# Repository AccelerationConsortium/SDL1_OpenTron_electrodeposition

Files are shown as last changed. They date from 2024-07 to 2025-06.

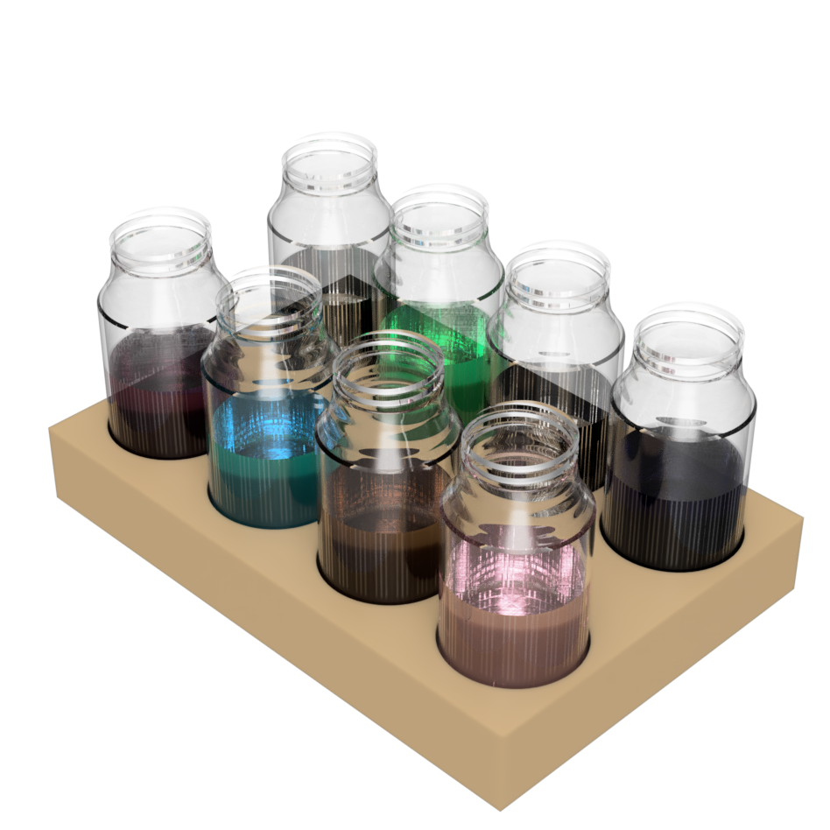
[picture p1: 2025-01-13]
3D_files/vial cartridge/assembly_vial_rack_2024-Sep-16_08-45-49AM-000_CustomizedView3837716591.png

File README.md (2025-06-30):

# SDL1_OpenTron_electrodeposition
This is the repository for the work done by external PhD researcher, Nis Fisker-Bødker from the Danish Technical University (DTU), while working at University of Toronto for the Acceleration Consortium.
The software combines the use of an opentron OT2 and a Sparkfun Arduino Uno to produce a facility for AI optimised electrodeposition of Oxygen Evolution Reaction (OER) catalyst for watersplitting in alkaline environment.

Please pay attention: Due to the Admiral Squidstat software, this will only work on a Windows X86_64 platform and not on Mac/Linux.

# 3D print and machine components
All files used for 3D printing, cutting and ordering at www.hubs.com can be found in /3D_files/. Consider to read the journal article "Democratizing self-driving lab platform for electrodeposition of catalyst and electrochemical validation" to understand the content.

# 1: Installation of Python environment
Install miniconda on your computer. Create an invironment for your opentron:
````
conda create -n opentron python=3.11
conda activate opentron
````

# 2: Download and install the SDL1_OpenTron_electrodeposition experiment
This is what is contained in this particular git-repo.

In a terminal with the correct python environment run:
````
git clone https://github.com/AccelerationConsortium/SDL1_OpenTron_electrodeposition.git
cd SDL1_OpenTron_electrodeposition
pip install -e .
````

# 3: Install requirement: Admiral Squidstat Plus potentiostat
On a Windows X86_64/AMD64 machine install the Admiral Instrument Squidstat software from the .exe file provided by the vendor. Afterwards install the Squidstat wheel provided with this release (/src/SquidstatPyLibrary-1.8.0.5-py3-none-win_amd64.whl) or download the newest wheel file from here:
https://github.com/Admiral-Instruments/AdmiralSquidstatAPI/tree/main/SquidstatLibrary/windows/pythonWrapper/Release

In a terminal within the right python environment and folder, run the command (adjust to your version if you downloaded another version of the wheel file):
````
pip install src/SquidstatPyLibrary-1.8.0.5-py3-none-win_amd64.whl
````

# 4: Install Arduino IDE and test the connection to your Arduino
Refer to Arduino documentation for this step and sparkfun.com for the additional components.
Set the right address for the temperature sensors and the quad relays as found in the firmware in src/arduino/main.ino. Here a summary as pseudocode is shown (don't try to use this directly in a .ino script):
````
// Quad relays
Relay_0-3 = 0x6D  // Default address
Relay_4-7 = 0x6C  // Modified address by programming

// Solid state relays for 110VAC/230VAC
Solid_state = 0x0A  // Default address

// Single relay 8
Relay_8 = 0x18  // Default address

// MCP9600 temperature sensor
tempSensor0 = 0x60  // Default address
tempSensor1 = 0x67  // Modified address by soldering on the PCB
````

Cable everything as according to the schematics in the journal article "AMPERE-2: An open-hardware, robotic platform for automated electrodeposition and electrochemical validation" and in the folder /manuals/Electric_diagram.pdf.
A bill of materials can be found in /manuals/Canada Electrodeposition Bill of Materials (BOM).xlsx

Once the firmware from /src/arduino/ has been uploaded to the Arduino, add a 10 micro farad capacitor between RESET and GND to avoid the PID regulation to reset itself all the time on the board.

# 5: Run the experiment
Examples are provided in /examples to both test the Admiral potentiostat, the Arduino, the opentron and the workflow with all machinary.

Run the experiment from the root of SDL1_OpenTron_electrodeposition/ by executing in an terminal:
````
python example/main.py
````

Please pay attention to the experiment.py. In case you are building your own experiment and workflow, this is the file you must edit to change the workflow of the robot, measurements etc.

# 6: Plotting of data via plot.py
Data (.csv and .jpeg plots) is placed in /data.
If you for some reason need to replot everything run the data/plot.py file.
````
python data/plot.py
````

# Important files
## parameters.py
It is very important to adjust /src/optenTron_electrodeposition/parameters.py to your setup. In here the positions on the openTron deck is defined as well as the chemicals, which relay on the arduino the chemical is attached etc. Spend a decent amount of time to familiarize yourself with the content.
In the future this should be integrated to a general robot_config.json
If you do change anything in parameters.py you must at the root of the SDL1_OpenTron_electrodeposition folder run the command again: 
````
pip install -e .
````

## experiment.py
This is basically the experiment. In the end of the class there is a method named run_experiment() which is basically the recipe of the experiment. Change it according to your needs.

## chemicals_left.txt
First of all sorry: This is a quick workaround to keep track of how much is in the bottles and vials on the setup. The experiment.py checks that it won't run dry by simple volume subtraction.
When refilling chemicals on the setup you must ensure that you also update this file acordingly with the new volumes.
In the future this should be integrated to a general robot_config.json

## last_processed_well.txt
Again sorry: This is a quick workaround to store the last processed well. Usually the openTron notation is eg. A1, A2, etc. but in this case it is from 0-14 with the 15 hole well I've used. Hole 14 is by the way occupied by a temperature sensor, so in reality you can only run from 0-13 wells.
The main reason it was used as a 0-14 number is because it was easier to iterate over numbers. In the future this should be integrated to a general robot_config.json

## metadata.csv
This file basically contains a table of all the experiments, their chemical combination, temperature, timestamp, overpotential during OER reaction at 10 mA/cm2 etc.
I would argue it is a good idea to keep something easy readable and comparable data like this in a single file.

## uid_run_number.txt
Every run has a unique ID which is tracked through this file.
In the future this should be integrated to a general robot_config.json

# Suggestions to future work
* Data should be placed elsewhere.
* SquidstatPyLibrary-XXX.whl should be replaced with an Admiral github and integrated into the pip installation of this repo.
* Move uid_run_number.txt, last_processed_well.txt, chemicals_left.txt, parameters.py into a robot_config.json file.
* Modify main.py to accept .json files with all the experiment variables. This file should then continuesly be populated with metadata about eg. how much was dispensed, in which order, time for each step, measurements etc. as the experiment progress.

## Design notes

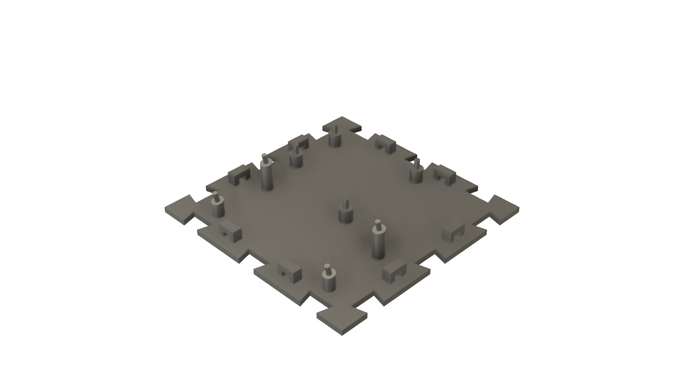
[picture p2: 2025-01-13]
3D_files/electronic tiles/1 arduino_and_screen_tile v14.png

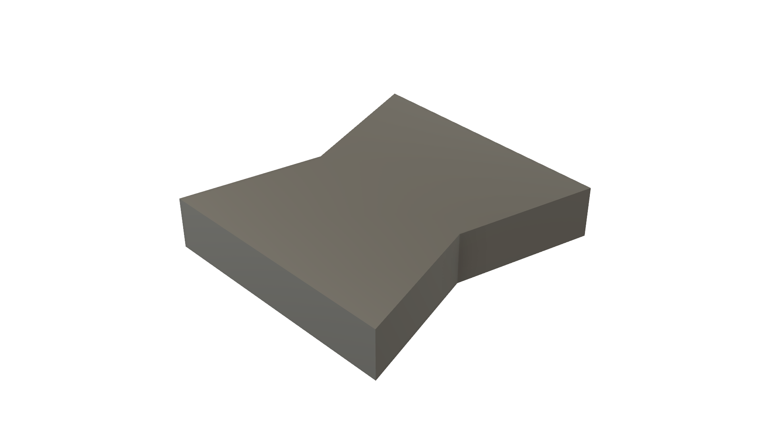
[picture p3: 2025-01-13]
3D_files/electronic tiles/tile_lock v3.png

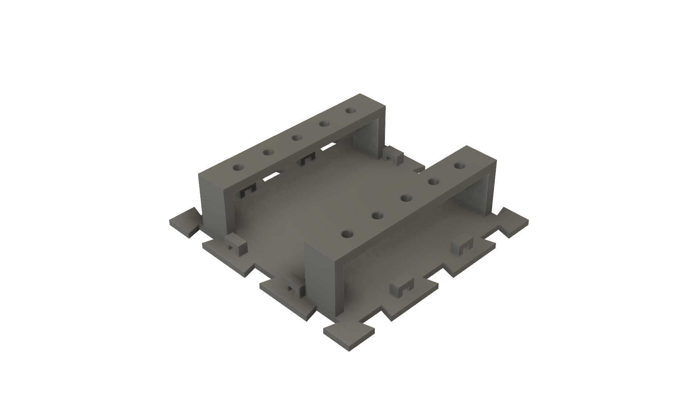
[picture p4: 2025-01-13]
3D_files/electronic tiles/9 terminal_tile v3.png

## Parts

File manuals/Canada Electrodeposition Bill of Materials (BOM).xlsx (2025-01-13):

Bill of Materials, Electrodeposition
Nis Fisker-Bødker, 16-04-2024
Tools |  |  |  |  |  | Minimum viable product | Fully utilized openTron
 | Item | Link | Cost per quantity | Quantity | Total
 | Makita Driver Drill | https://www.amazon.ca/Makita-DHP482Z-Hammer-Driver-Drill/dp/B01C85KSVU | 99.99 CAD | 1 | 99.99 CAD
 | Makita Battery | https://www.amazon.ca/Makita-Y-00309-Li-Ion-Battery-Charger/dp/B075SM1LHH | 127.00 CAD | 1 | 127.00 CAD
 | Tap drill set | https://www.amazon.ca/Neiko-10059A-Combination-Change-Adapter/dp/B0762HJ3GF | 45.00 CAD | 1 | 45.00 CAD
 | Drill set | https://www.amazon.ca/Bosch-CO21-Cobalt-Metal-Drill/dp/B06XY7W87H | 55.00 CAD | 1 | 55.00 CAD
 | Conedrill etc | https://www.amazon.ca/NordWolf-12-Piece-Countersink-Automatic-Compatible/dp/B083NWL5D2 | 60.00 CAD | 1 | 60.00 CAD
 | Metal saw | https://www.amazon.ca/Craftsman-Hand-12-Inch-Hacksaw-CMHT20138/dp/B07R92S9YZ | 16.00 CAD | 1 | 16.00 CAD
 | Estimated freight |  |  |  | 40.30 CAD
 | Total |  |  |  | 443.29 CAD
Hardware | Cartridge base
 | Item | Link | Cost per quantity | Quantity | Total
 | Aluminum base (bottom) | hubs.com | 110.00 CAD | 2 | 220.00 CAD
 | Aluminum base (top) | hubs.com | 110.00 CAD | 2 | 220.00 CAD
 | M3 8x8 Rubber shock absorbers | https://www.amazon.ca/Rubber-Absorber-Vibration-Silentblock-Bobbins/dp/B07H2BW3CX | 9.17 CAD | 2 | 18.34 CAD
 | Ultrasonic transducer | https://www.amazon.ca/Baglaum-Ultrasonic-Transducer-Cleaning-Machines/dp/B0CRYQLTQN | 50.23 CAD | 2 | 100.46 CAD
 | Flat heating element 110V | https://www.amazon.ca/PTCYIDU-Insulated-Temperature-Thermostatic-Miniature/dp/B0CDKTLXWJ | 26.92 CAD | 2 | 53.84 CAD
 | Pt100 thermocouple | https://www.sparkfun.com/products/251 | 17.00 CAD | 2 | 34.00 CAD
 | Temperature sensor MCP9600 | https://www.sparkfun.com/products/16295 | 22.50 CAD | 2 | 45.00 CAD
 | Nickel Pt100 sleeve (corossion resistant) | https://www.amazon.com/Temperature-Deep-Drawing-DS18B20-Thermowell-ThermocoupleProtection/dp/B0C61VT83G | 20.00 CAD | 1 | 20.00 CAD
 | Aluminum rod ø10mm | https://www.amazon.ca/MECCANIXITY-Round-Aluminum-Diameter-Length/dp/B09Y24WWGP | 20.00 CAD | 2 | 40.00 CAD
 | M3, M4 screws flat head | https://www.amazon.ca/Hilitchi-460-Piece-Metric-Countersunk-Assortment/dp/B06Y3JDM4R | 23.00 CAD | 1 | 23.00 CAD
 | M4 threaded rod 60mm | https://www.amazon.ca/uxcell-Threaded-Stainless-Threads-M4-0-7/dp/B09L68MJJ5 | 9.00 CAD | 1 | 9.00 CAD
 | Sparkfun Arduino | https://www.sparkfun.com/products/18158 | 21.50 CAD | 1 | 21.50 CAD
 | Sparkfun LCD | https://www.sparkfun.com/products/16396 | 22.00 CAD | 1 | 22.00 CAD
 | Sparkfun AC Solid state relay 110V | https://www.sparkfun.com/products/16810 | 95.00 CAD | 1 | 95.00 CAD
 | Sparkfun Qwiic cable | https://www.sparkfun.com/products/15081 | 9.00 CAD | 1 | 9.00 CAD
 | M3, M4 washers | https://www.amazon.ca/260-Pcs-7-Size-QTEATAK-Stainless-Assortment/dp/B07LCB92CB | 14.00 CAD | 1 | 14.00 CAD
 | M4 wing nut | https://www.amazon.ca/uxcell-Stainless-Fasteners-Hurrican-Butterfly/dp/B07QB5NKDG | 13.50 CAD | 1 | 13.50 CAD
 | Heat paste | https://www.amazon.ca/BSFF-Compound-Heatsink-Processor-Performance/dp/B09NLXX61M | 16.00 CAD | 1 | 16.00 CAD
 | Estimated freight |  |  |  | 95.86 CAD
 | Total |  |  |  | 1070.50 CAD | 1070.50 CAD | 11775.54 CAD
Hardware | Well cartridge
 | Item | Link | Cost per quantity | Quantity | Total
 | Aluminum base | xometry.com | 110.00 CAD | 1 | 110.00 CAD
 | Nickel tape 0,2mm thickness | https://www.amazon.ca/GOONSDS-Nickel-Plate-Sheet-0-2x100x1000mm/dp/B09879LSZC | 69.00 CAD | 1 | 69.00 CAD
 | Double sided tape | https://www.amazon.ca/Premium-Double-Sided-Adhesive-Tape/dp/B07B5YBN3Y | 15.50 CAD | 1 | 15.50 CAD
 | Gasgets | https://www.amazon.ca/uxcell-Silicone-Ring-Width-Gasket/dp/B07CVJMN2M | 8.99 CAD | 2 | 17.98 CAD
 | PP plastic top | xometry.com | 376.00 CAD | 1 | 376.00 CAD
 | (alternatively PEEK) | hubs.com | 576.00 CAD | 0 | 0.00 CAD
 | Estimated freight |  |  |  | 58.85 CAD
 | Total |  |  |  | 647.33 CAD | 647.33 CAD | 6473.28 CAD
Hardware | Robotic mount
 | Item | Link | Cost per quantity | Quantity | Total
 | Nickel rod ø 10mm | https://www.amazon.ca/RINGGLO-Antioxidant-Activity-Scientific-Experiment/dp/B0CCMD16QV | 35.87 CAD | 1 | 35.87 CAD
 | Mini Hydroflex reference electrode | https://gaskatel.de/en/shop/mini-hydrogen-reference-electrode-mini-hydroflex/ | 308.00 CAD | 1 | 308.00 CAD
 | Platinum electrode | https://www.amazon.ca/Platinum-Electrode-99-99-10mm-Customized-Specifications/dp/B0CP8XHCZ6 | 285.00 CAD | 1 | 285.00 CAD
 | Platinum wire | https://www.amazon.ca/Platinum-Wire-gauge-99-9-6-inches/dp/B003E2Y2T6 | 56.00 CAD | 1 | 56.00 CAD
 | Electrical wire | https://www.amazon.ca/CBAZY-Stranded-Flexible-Silicone-Electric/dp/B073RDG2J6 | 25.00 CAD | 1 | 25.00 CAD
 | Solder connecters | https://www.amazon.ca/Connectors-Sopoby-Waterproof-Electrical-Automotive/dp/B07R4Z13P3 | 30.00 CAD | 1 | 30.00 CAD
 | Wire connectors | https://www.amazon.ca/Compact-Splicing-Connector-Assortment-221-2401/dp/B0BXQG6RLQ | 58.42 CAD | 1 | 58.42 CAD
 | Banana plug terminals | https://www.amazon.ca/Speaker-Terminal-Binding-Adapter-Connector/dp/B07C2P4YNB | 12.09 CAD | 1 | 12.09 CAD
 | Hoop and loop tape | https://www.amazon.ca/gp/product/B0BZXMHKRB/ref=ewc_pr_img_1?smid=AHCEK5ZEJTURN&psc=1 | 24.99 CAD | 1 | 24.99 CAD
 | Single relay to switch between Counter and Reference | https://www.sparkfun.com/products/15093 | 20.00 CAD | 1 | 20.00 CAD
 | Qwiic multiplexer | https://www.sparkfun.com/products/18012 | 3.00 CAD | 3 | 9.00 CAD
 | Qwiic long cables | https://www.sparkfun.com/products/17257 | 3.00 CAD | 3 | 9.00 CAD
 | Cable shoes | https://www.amazon.ca/Disconnect-Electrical-Solderless-Connectors-Assortment/dp/B01E4RAVI0 | 22.00 CAD | 1 | 22.00 CAD
 | DC connector for quad relay | https://www.sparkfun.com/products/10287 | 3.50 CAD | 2 | 7.00 CAD
 | Plate for supporting electronics |  | 110.00 CAD | 1 | 110.00 CAD
 | Machine shop cut of 8x Ø10mm alu legs incl. tapping M3 |  | 80.00 CAD | 1 | 80.00 CAD
 | 3D printer filament |  | 40.00 CAD | 2 | 80.00 CAD
 | 3D resin printing of flush tool |  | 40.00 CAD | 1 | 40.00 CAD
 | Estimated freight |  |  |  | 81.04 CAD
 | Total |  |  |  | 1293.41 CAD | 1293.41 CAD | 1293.41 CAD
Hardware | Cleaning cartridge
 | Item | Link | Cost per quantity | Quantity | Total
 | PP plastic top | xometry.com | 300.00 CAD | 1 | 300.00 CAD
 | Aluminum base | xometry.com | 110.00 CAD | 1 | 110.00 CAD
 | Peristaltic pump | https://www.amazon.ca/peristaltic-Kamoer-KPHM100-Service-high-Precision/dp/B09F69KYF3 | 20.00 CAD | 6 | 120.00 CAD
 | Silicone tubing 5mm OD, 3mm ID | https://www.amazon.ca/Yesallwas-Silicone-Flexible-Rubber-Transfer/dp/B07S5LL4HR | 16.00 CAD | 1 | 16.00 CAD
 | 12V DC supply | https://www.amazon.ca/Waterproof-Converter-Transformer-Voltage-3-Prong/dp/B08ZJZPF4Y | 44.00 CAD | 1 | 44.00 CAD
 | 12V relay | https://www.sparkfun.com/products/16566 | 32.50 CAD | 2 | 65.00 CAD
 | Cable zip ties | https://www.amazon.ca/BESTIN-Self-Locking-Black-Nylon-12-Inch/dp/B0977LP2KQ | 19.00 CAD | 1 | 19.00 CAD
 | Estimated freight |  |  |  | 67.40 CAD
 | Total |  |  |  | 741.40 CAD | 741.40 CAD | 741.40 CAD
Chemicals | Consumables
 | Item | Link | Cost per quantity | Quantity | Total
 | 500 FeCl3 |  | 592.00 CAD | 1 | 592.00 CAD
 | 500g CoCl2 salt |  | 43.00 CAD | 1 | 43.00 CAD
 | 500g ZnCl3 |  | 108.00 CAD | 1 | 108.00 CAD
 | 100 g CuCl2 |  | 50.00 CAD | 1 | 50.00 CAD
 | 500g MnCl2 |  | 64.00 CAD | 1 | 64.00 CAD
 | 125g CrCl3 |  |  | 1 | 0.00 CAD
 | 500g NiCl2 |  |  | 1 | 0.00 CAD
 | 4L Ammonium hydroxide NH4OH |  |  | 1 | 0.00 CAD
 | 500g potassium citrate |  |  | 1 | 0.00 CAD
 | Hydrocloric aeid 1M / 1N 2L |  |  | 1 | 0.00 CAD
 | DI water 8L |  |  | 1 | 0.00 CAD
 | Bottles for chemicals 6+9 500ml |  | 64.00 CAD | 2 | 128.00 CAD
 | Chemstore misc. Like beakers, vials etc. |  | 206.00 CAD | 1 | 206.00 CAD
 | Estimated freight |  |  |  | 85.70 CAD
 | Total |  |  |  | 1276.70 CAD | 1276.70 CAD | 1276.70 CAD
 |  |  |  |  |  | 5029.34 CAD | 21560.33 CAD

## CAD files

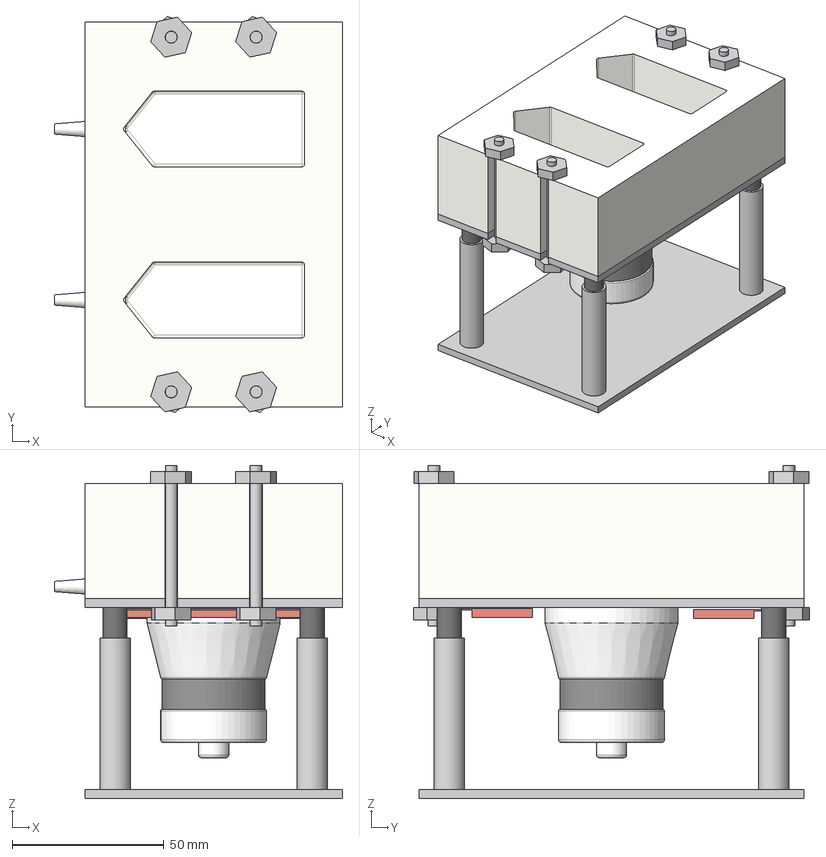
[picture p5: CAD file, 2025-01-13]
3D_files/cleaning cartridge/assembly_cleaning_cartridge v15.step
95.0 x 130.6 x 110.0 mm
cleaning_bath_bolt x 4
cartridge_bottom
rubber_dampener x 4
alu_legs x 4
cartridge_top
ultrasound
heating_element
heating_element_rotated
Cleaning_bath

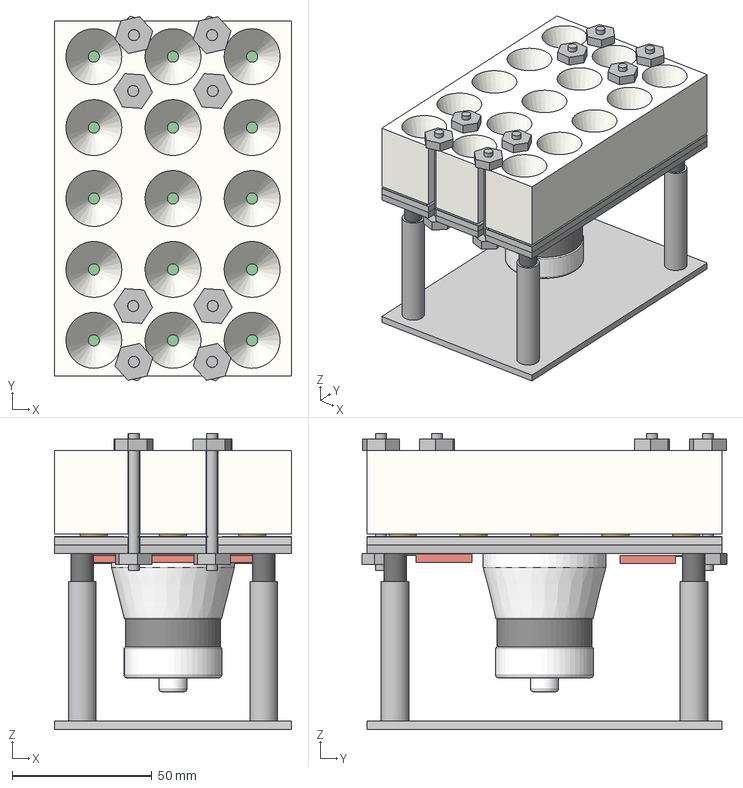
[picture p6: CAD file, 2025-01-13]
3D_files/well cartridge/assembly_well_cartridge v44.step
85.0 x 130.6 x 106.0 mm
well_cartridge_bolt x 4
cartridge_bottom
rubber_dampener x 4
alu_legs x 4
cartridge_top
ultrasound
heating_element
heating_element_rotated
nickel_layer x 3
1_well_catridge_ultrasound_mount
well_cartridge_bolt_top x 4
3_well_cartridge_test_cell

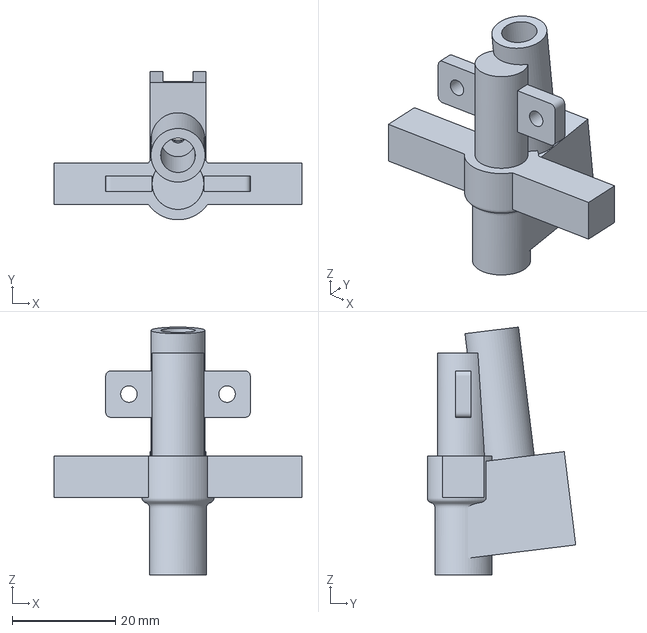
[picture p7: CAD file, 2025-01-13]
3D_files/3Dprint/platinum_silver_electrode v7.3mf
48.0 x 28.7 x 48.0 mm

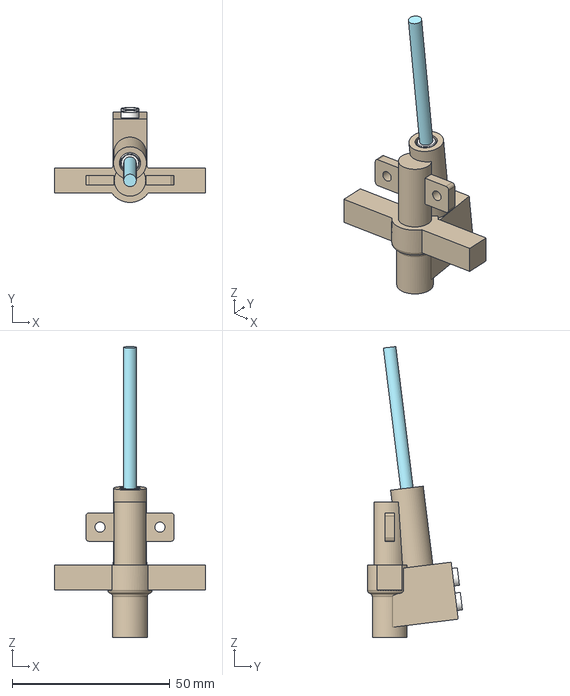
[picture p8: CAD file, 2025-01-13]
3D_files/agcl electrode tool/platinum_silver_electrode v9.step
48.0 x 30.1 x 92.2 mm
cable_terminal
silver_reference_electrode

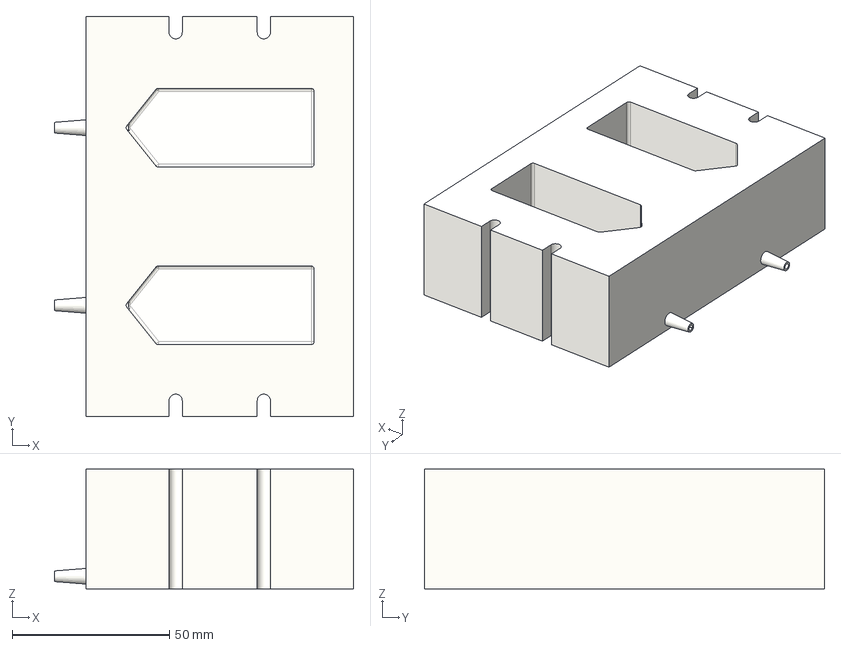
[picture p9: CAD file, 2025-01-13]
3D_files/Cleaning_bath v7.step
95.0 x 127.0 x 38.0 mm

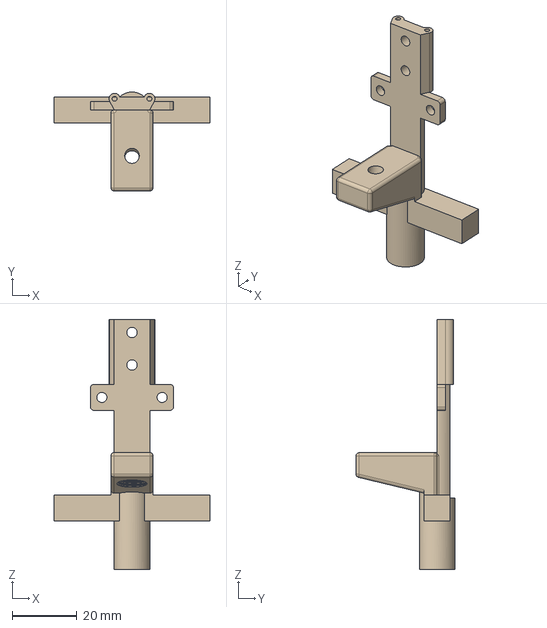
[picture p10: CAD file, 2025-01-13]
3D_files/electrochemical test tool/platinum_electrode v46.step
48.0 x 30.5 x 77.0 mm

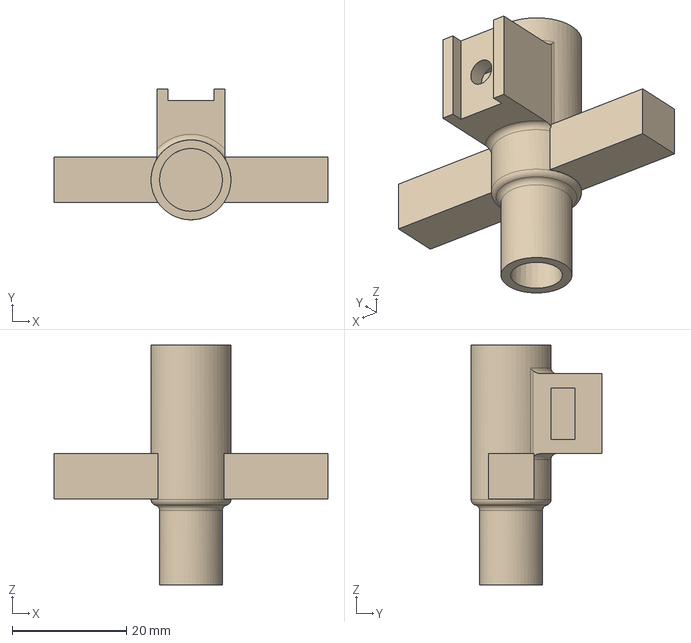
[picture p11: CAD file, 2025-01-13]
3D_files/electrodeposition tool/nickel_electrode v30.step
48.0 x 22.9 x 42.0 mm

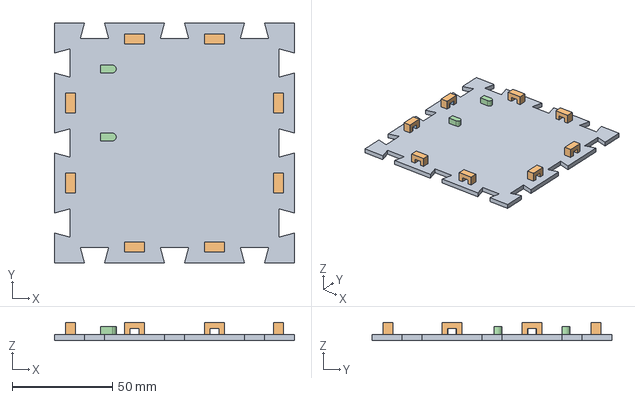
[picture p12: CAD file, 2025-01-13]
3D_files/electronic tiles/4 Power_source1 v18.step
120.0 x 120.0 x 9.00 mm

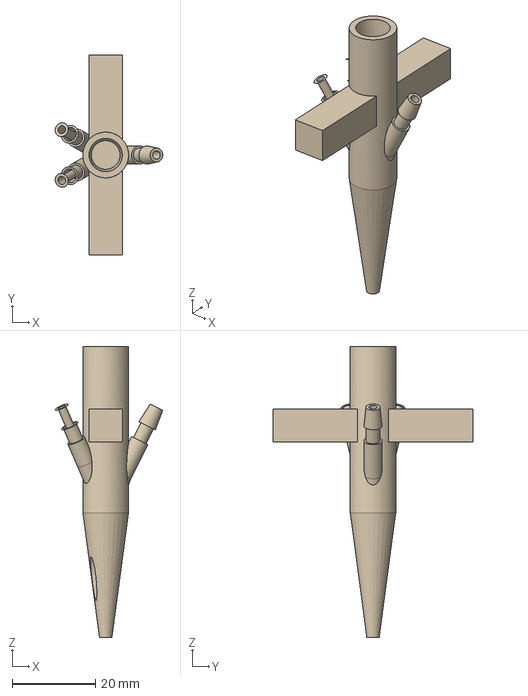
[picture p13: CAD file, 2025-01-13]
3D_files/flush tool/Flush_tool v11.step
25.9 x 48.0 x 70.0 mm

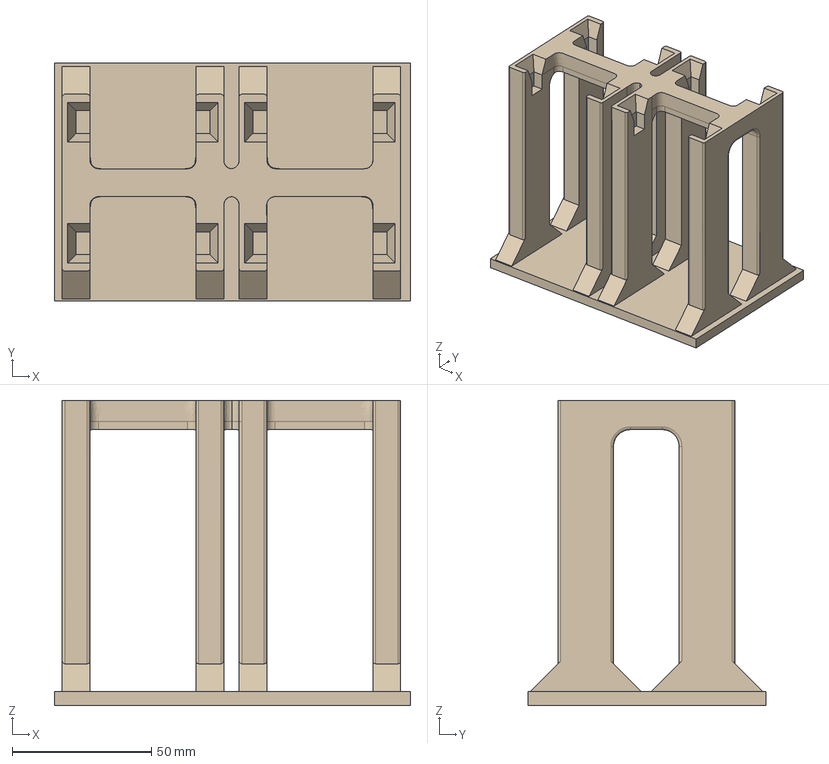
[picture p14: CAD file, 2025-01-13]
3D_files/tool cartridge/tool_cartridge_v7.step
127.8 x 85.5 x 109.5 mm

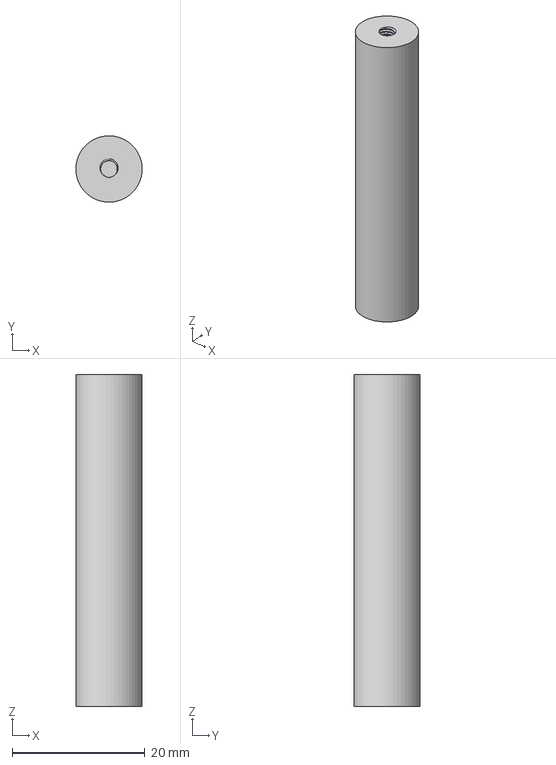
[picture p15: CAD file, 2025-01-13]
3D_files/ultrasonic cartridge base/alu_legs v3.step
9.99 x 10.00 x 50.0 mm

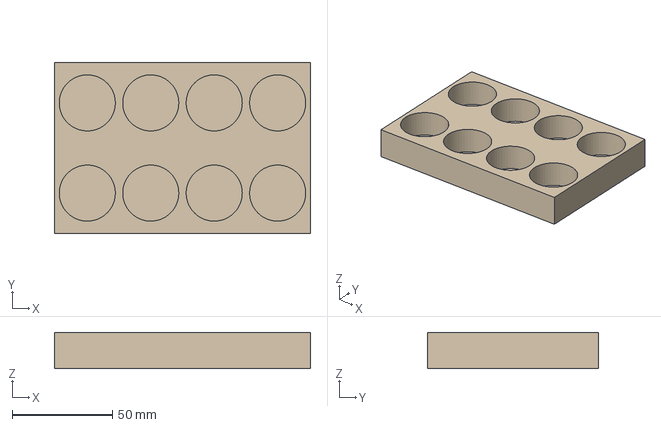
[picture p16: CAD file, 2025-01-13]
3D_files/vial cartridge/vial_rack v3.step
127.8 x 85.5 x 18.0 mm

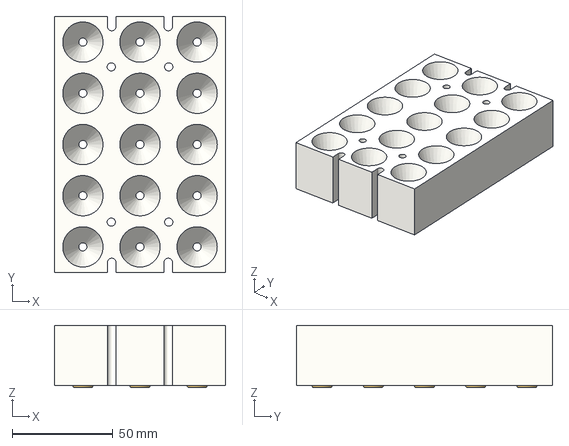
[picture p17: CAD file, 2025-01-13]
3D_files/well cartridge/well_cartridge_v24_CNCmachined_PE.step
85.0 x 127.0 x 31.0 mm

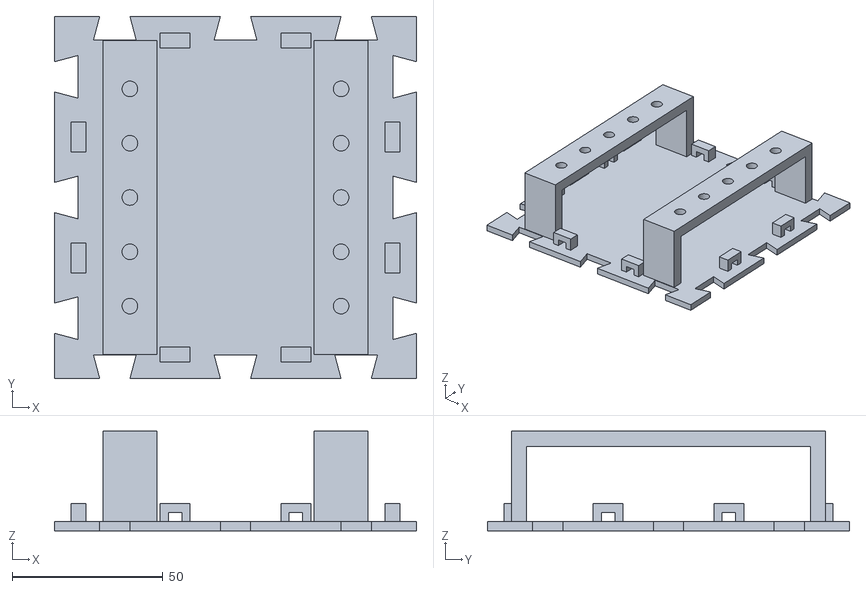
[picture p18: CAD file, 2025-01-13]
3D_files/3Dprint/9 terminal_tile v2.stl
120.0 x 120.0 x 33.0

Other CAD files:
3D_files/agcl electrode tool/platinum_silver_electrode v9 -only_plastic_for_printing.step
3D_files/cartridge_bottom v1.step
3D_files/cleaning cartridge/Cleaning_bath v9.step
3D_files/1_well_catridge_ultrasound_mount v5.step
3D_files/3Dprint/1 arduino_and_screen_tile v12.stl
3D_files/3Dprint/3_well_cartridge_test_cell v21.stl
3D_files/3Dprint/Cleaning_bath v7.stl
3D_files/3Dprint/Electrical_connections v5.stl
3D_files/3Dprint/Flush_tool_Eloise v10.stl
3D_files/3Dprint/Flush_tool_Eloise v7.stl
3D_files/3Dprint/Flush_tool_Eloise v9.stl
3D_files/3Dprint/Power_source1 v16.stl
3D_files/3Dprint/Power_source2 v11.stl
3D_files/3Dprint/Quad_relay v6.stl
3D_files/3Dprint/Thread test v1.stl
3D_files/3Dprint/alu_legs v3.stl
3D_files/3Dprint/arduino_and_screen_tile v9.stl
3D_files/3Dprint/cleaning_cartridge_bracket v2.stl
3D_files/3Dprint/cleaning_cartridge_bracket v3.stl
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

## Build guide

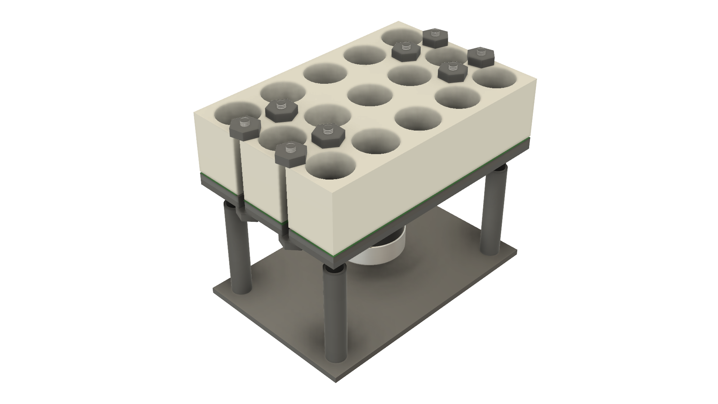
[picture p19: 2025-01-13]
3D_files/well cartridge/assembly_well_cartridge v44.png

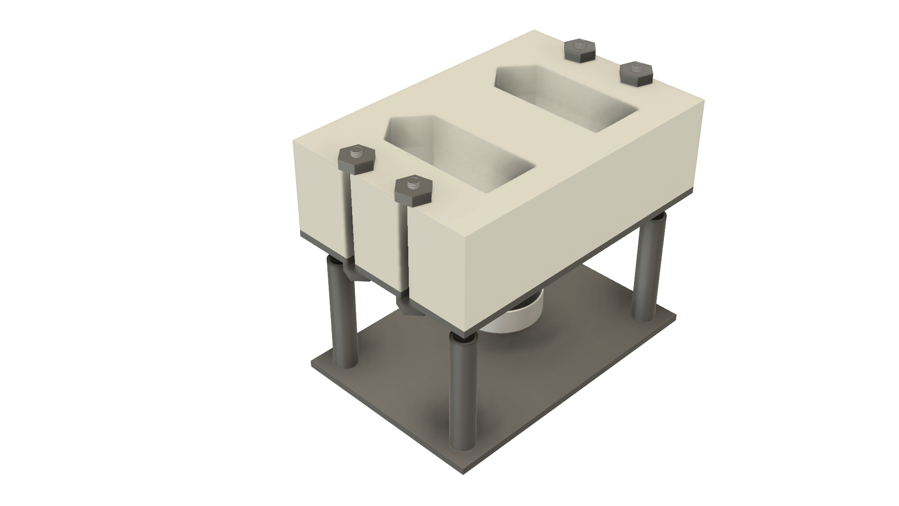
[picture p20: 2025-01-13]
3D_files/cleaning cartridge/assembly_cleaning_cartridge v14.png

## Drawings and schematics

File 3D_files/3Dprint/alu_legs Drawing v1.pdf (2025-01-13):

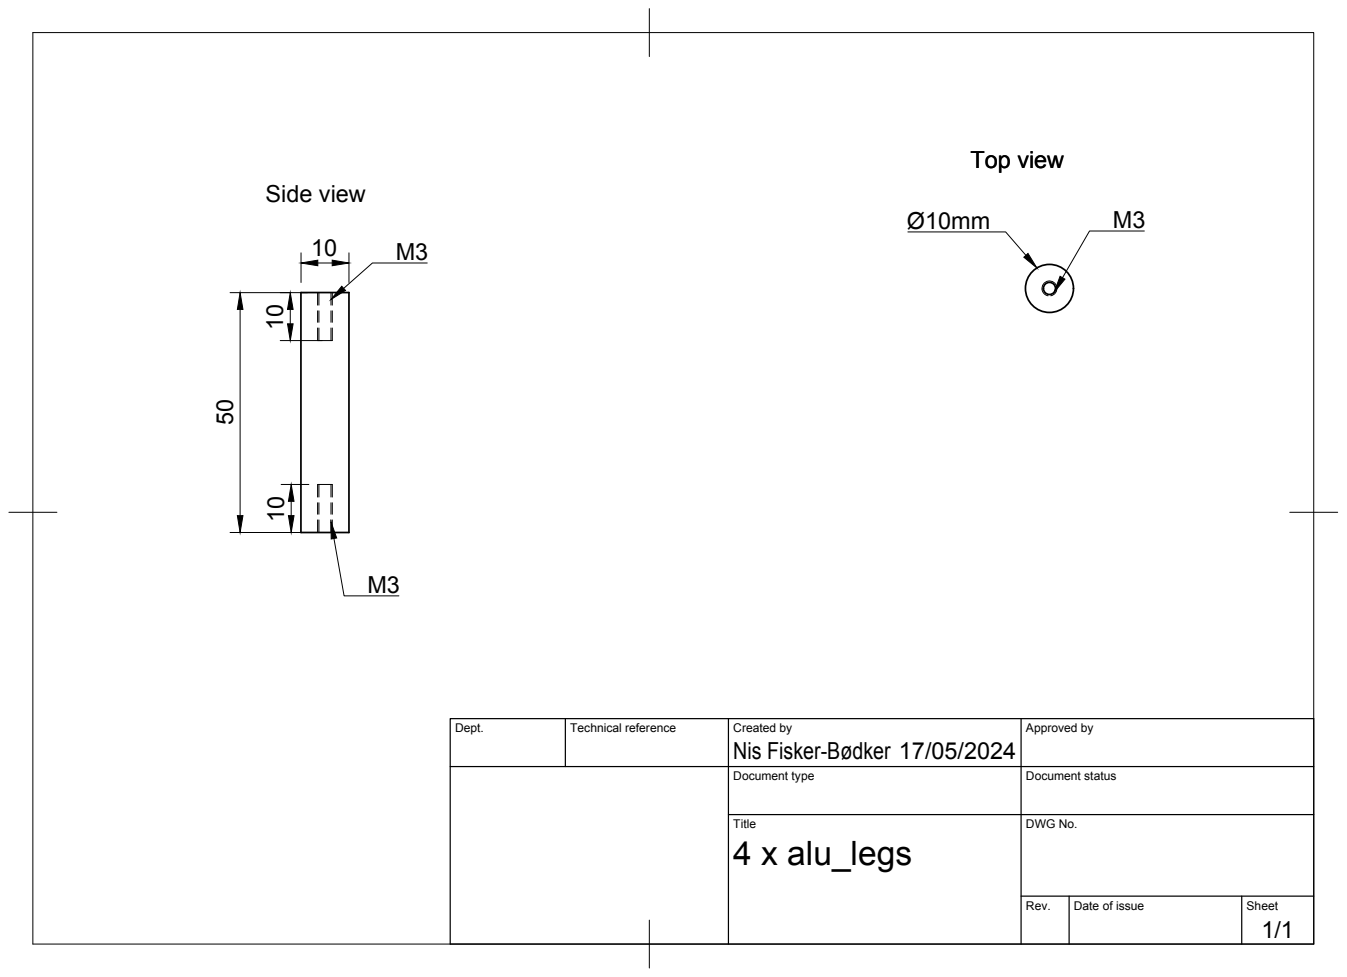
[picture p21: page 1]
Top view; Side view

Dept. | Technical reference | Created by Nis Fisker-Bødker 17/05/2024 | Approved by

Document type | Document status

Title 4 x alu_legs | DWG No.

Rev. | Date of issue | Sheet 1/1

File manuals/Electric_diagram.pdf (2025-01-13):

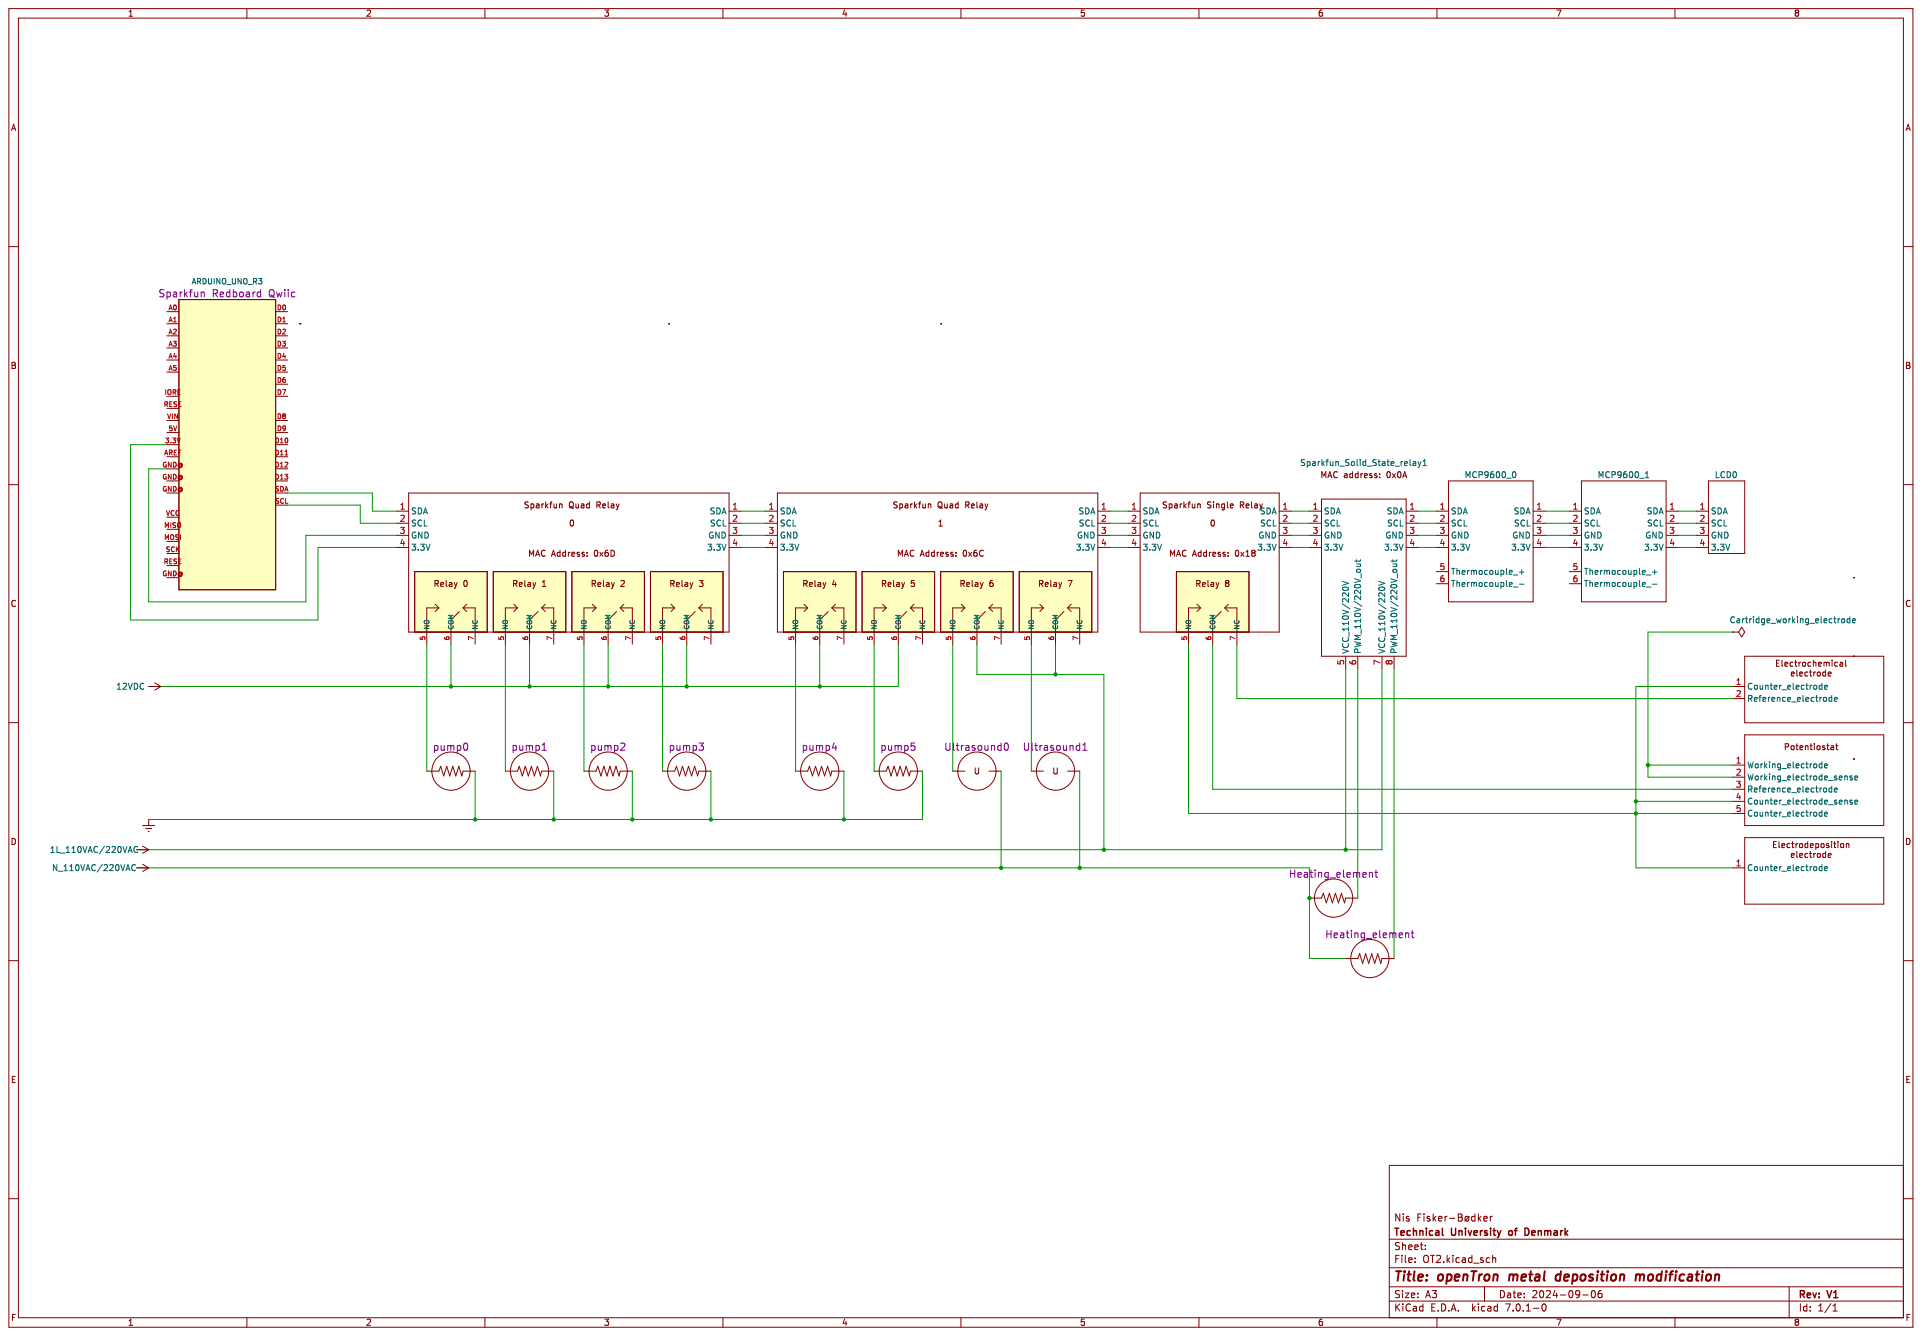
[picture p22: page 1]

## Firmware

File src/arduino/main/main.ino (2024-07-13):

/*
  Software written by
  Nis Fisker-Bødker
  nis.fisker@gmail.com
  2024 at University of Toronto

  Components used:
  Sparkfun Arduino Redboard with Qwiic
  2 x SparFun MCP9600 (for temperature measurements in liquids)
  1 x SparkFun Dual Solid State Relay (for heat control)
  1 x Sparkfun Quad Relay (for control of peristaltic pumps)
  1 x Sparkfun SerLCD
  1 x Sparkfun single relay (for control of electrode connection)

*/
#include <Wire.h>
#include <EEPROM.h>
const byte buff_size = 40;
char input_buffer[buff_size];
const char start_marker = '<';
const char end_marker = '>';
byte bytes_rcvd = 0;
boolean read_in_progress = false;
boolean new_data_pc = false;
String message_from_pc;
int direction_in = 0;
int steps_in = 0;
int step_time_in = 0;
int m_num = 0;
float ultrasound_time_in;


/*
   Load temperature sensor
*/
#include <SparkFun_MCP9600.h>
MCP9600 tempSensor0;
float sample_temperature0;
float ambient_temperature0;
MCP9600 tempSensor1;
float sample_temperature1;
float ambient_temperature1;

/*
   Load LCD
*/

#include <SerLCD.h>
SerLCD lcd;  // Initialize the library with default I2C address 0x72


/*
   Load relays
*/
// Relay 0-3
#include <SparkFun_Qwiic_Relay.h>
#define RELAY_ADDR 0x6D  // Alternate address 0x6C
Qwiic_Relay quadRelay(RELAY_ADDR);

// Solid state relays for 110VAC
#define RELAY_SOLIDSTATE 0x0A
Qwiic_Relay solidStateRelay(RELAY_SOLIDSTATE);

// Relay 4-7
// Remember this is NOT a standard I2C add - it was coded to the quad relay.
#define RELAY_ADDR2 0x6C  // 0x09
Qwiic_Relay quadRelay2(RELAY_ADDR2);

// Relay 8
#define RELAY_ADDR3 0x18
Qwiic_Relay singleRelay3(RELAY_ADDR3);

/*
   Load PID control
*/
#include <AutoPID.h>
#define OUTPUT_MIN 0
#define OUTPUT_MAX 255
#define KP0 .12
#define KI0 0.5
#define KD0 1
#define KP1 .12
#define KI1 0.5
#define KD1 1
double temperature0, outputVal0;
double temperature1, outputVal1;
double setPoint0;
double setPoint1;
AutoPID PID0(&temperature0, &setPoint0, &outputVal0, OUTPUT_MIN, OUTPUT_MAX, KP0, KI0, KD0);
AutoPID PID1(&temperature1, &setPoint1, &outputVal1, OUTPUT_MIN, OUTPUT_MAX, KP1, KI1, KD1);
unsigned long lastTempUpdate;  //tracks clock time of last temp update
int dutyCycle0 = 0;            //Tracks how much the relay is on at 1Hz. 120 = 100%.
int dutyCycle1 = 0;            //Tracks how much the relay is on at 1Hz. 120 = 100%.

void setup() {
  Serial.begin(115200);
  Wire.begin();
  Wire.setClock(100000);


  /*
     Setup LCD
  */
  // Serial.println("Booting LCD");
  lcd.begin(Wire);                  //Set up the LCD for I2C communication
  lcd.setBacklight(255, 255, 255);  //Set backlight to bright white
  lcd.setContrast(5);               //Set contrast. Lower to 0 for higher contrast.
  lcd.clear();                      //Clear the display - this moves the cursor to home position as well
  lcd.print("Booting!");


  /*
     Setup relays
  */
  if (!quadRelay.begin()) {
    lcd.setCursor(0, 0);
    lcd.print("Quad relay not connected");
    Serial.println("Check connections to Qwiic Relay 0-3.");
    delay(2000);
  }
  if (!solidStateRelay.begin()) {
    lcd.setCursor(0, 0);
    lcd.print("SolStateRelay not connected");
    Serial.println("Check connections to solid state relay.");
    delay(2000);
  }
  if (!quadRelay2.begin()) {
    lcd.setCursor(0, 0);
    lcd.print("Quad relay not connected");
    Serial.println("Check connections to Qwiic Relay 4-7.");
    delay(2000);
  }
  if (!singleRelay3.begin()) {
    lcd.setCursor(0, 0);
    lcd.print("Single relay not connected");
    Serial.println("Check connections to Qwiic Relay 8.");
    delay(2000);
  }

  /*
     Setup temperature sensor 0
  */
  // Serial.println("Booting temperature sensors");
  tempSensor0.begin(0x60);  // Uses the default address (0x60) for SparkFun Thermocouple Amplifier
  tempSensor1.begin(0x67);

  // Check if temperature sensor is connected
  // Serial.println("Check if temperature sensor 0 is online");
  if (!tempSensor0.isConnected()) {
    lcd.setCursor(0, 0);
    lcd.print("Temp 0 not connected");
    Serial.println("Temperature sensor 0 not connected");
    delay(10000);
  }

  // Check if the temperature sensor address is correct
  // Serial.println("Check temperature sensor 0 address");
  if (!tempSensor0.checkDeviceID()) {
    lcd.setCursor(0, 0);
    lcd.print("Temp 0 addr. is wrong");
    Serial.println("Temperature sensor 0 address is wrong");
    delay(10000);
  }


  /*
     Setup temperature sensor 1
  */
  // Check if temperature sensor 1 is connected
  // Serial.println("Check if temperature sensor 1 is online");
  if (!tempSensor1.isConnected()) {
    lcd.setCursor(0, 0);
    lcd.print("Temp 1 not connected");
    Serial.println("Temperature sensor 1 not connected");
    delay(10000);
  }

  // Check if the temperature sensor address is correct
  // Serial.println("Check temperature sensor 1 address");
  if (!tempSensor1.checkDeviceID()) {
    lcd.setCursor(0, 0);
    lcd.print("Temp 1 addr. is wrong");
    Serial.println("Temperature sensor 1 address is wrong");
    delay(10000);
  }



  /*
     Setup PID control
  */
  read_from_eeprom_setPoints();

  // if temperature is more than 4 degrees below or above setpoint, OUTPUT will be set to min or max respectively
  PID0.setBangBang(2);
  PID1.setBangBang(2);
  //set PID update interval to 1200ms
  PID0.setTimeStep(1200);
  PID1.setTimeStep(1200);

  lcd.clear();
}

void loop() {
  // Updating the sensor values
  delay(1000);
  sample_temperature0 = read_sample_temperature(0);
  sample_temperature1 = read_sample_temperature(1);



  // Update PID controller 0
  temperature0 = sample_temperature0;
  PID0.run();
  if (outputVal0 > 0) {
    dutyCycle0 = (outputVal0 / 255) * 120;
  } else {
    dutyCycle0 = 0;
  }
  solidStateRelay.setSlowPWM(1, dutyCycle0);

  // Update PID controller 1
  temperature1 = sample_temperature1;
  PID1.run();
  if (outputVal1 > 0) {
    dutyCycle1 = (outputVal1 / 255) * 120;
  } else {
    dutyCycle1 = 0;
  }
  solidStateRelay.setSlowPWM(2, dutyCycle1);

  // Write the sensor values to the LCD
  write_to_lcd(sample_temperature0, sample_temperature1, dutyCycle0, dutyCycle1);


  // Check if there is instructions from the PC
  get_data_from_pc();
}

void get_data_from_pc() {

  // receive data from PC and save it into input_buffer
  while (Serial.available()) {
    char x = Serial.read();

    // the order of these IF clauses is significant

    if (x == end_marker) {
      read_in_progress = false;
      new_data_pc = true;
      input_buffer[bytes_rcvd] = 0;
      parse_data();
    }

    if (read_in_progress) {
      input_buffer[bytes_rcvd] = x;
      bytes_rcvd++;
      if (bytes_rcvd == buff_size) {
        bytes_rcvd = buff_size - 1;
      }
    }

    if (x == start_marker) {
      bytes_rcvd = 0;
      read_in_progress = true;
    }
  }
}

void parse_data() {
  // split the data into its parts
  char *str_to_ind;  // this is used by strtok() as an index

  str_to_ind = strtok(input_buffer, ",");  // get the first part - the string
  message_from_pc = String(str_to_ind);

  if (message_from_pc == "set_relay_on_time") {
    str_to_ind = strtok(NULL, ",");    // this continues where the previous call left off
    int relay_num = atoi(str_to_ind);  // convert this part to an integer

    str_to_ind = strtok(NULL, ",");
    int time_ms = atoi(str_to_ind);

    if (0 <= relay_num && relay_num <= 3)  // First quad relay
    {
      int relay = relay_num + 1;
      quadRelay.turnRelayOn(relay);
      delay(time_ms);
      quadRelay.turnRelayOff(relay);
    }
    if (4 <= relay_num && relay_num <= 7)  // Second quad relay
    {
      int relay = relay_num - 3;
      quadRelay2.turnRelayOn(relay);
      delay(time_ms);
      quadRelay2.turnRelayOff(relay);
    }
    if (8 == relay_num)  // Single relay
    {
      singleRelay3.turnRelayOn();
      delay(time_ms);
      singleRelay3.turnRelayOff();
    }
    Serial.println("#");  // '#' indicates process is done
  }

  if (message_from_pc == "set_relay_on") {
    str_to_ind = strtok(NULL, ",");    // this continues where the previous call left off
    int relay_num = atoi(str_to_ind);  // convert this part to an integer

    if (0 <= relay_num && relay_num <= 3)  // First quad relay
    {
      int relay = relay_num + 1;
      quadRelay.turnRelayOn(relay);
    }
    if (4 <= relay_num && relay_num <= 7)  // Second quad relay
    {
      int relay = relay_num - 3;
      quadRelay2.turnRelayOn(relay);
    }
    if (8 == relay_num)  // Single relay
    {
      singleRelay3.turnRelayOn();
    }
    Serial.println("#");  // '#' indicates process is done
  }

  if (message_from_pc == "set_relay_off") {
    str_to_ind = strtok(NULL, ",");    // this continues where the previous call left off
    int relay_num = atoi(str_to_ind);  // convert this part to an integer

    if (0 <= relay_num && relay_num <= 3)  // First quad relay
    {
      int relay = relay_num + 1;
      quadRelay.turnRelayOff(relay);
    }
    if (4 <= relay_num && relay_num <= 7)  // Second quad relay
    {
      int relay = relay_num - 3;
      quadRelay2.turnRelayOff(relay);
    }
    if (8 == relay_num)  // Single relay
    {
      singleRelay3.turnRelayOff();
    }
    Serial.println("#");  // '#' indicates process is done
  }


  if (message_from_pc == "read_temp0") {
    Serial.println(sample_temperature0);
  }
  if (message_from_pc == "read_temp1") {
    Serial.println(sample_temperature1);
  }
  if (message_from_pc == "read_temp0_ambient") {
    Serial.println(ambient_temperature0);
  }
  if (message_from_pc == "read_temp1_ambient") {
    Serial.println(ambient_temperature1);
  }
  if (message_from_pc == "setpoint0") {
    str_to_ind = strtok(NULL, ",");  // this continues where the previous call left off
    setPoint0 = atoi(str_to_ind);
    setPoint0 = setPoint0 / 10;
    write_to_eeprom_setPoint0(setPoint0);
  }
  if (message_from_pc == "setpoint1") {
    str_to_ind = strtok(NULL, ",");  // this continues where the previous call left off
    setPoint1 = atoi(str_to_ind);
    setPoint1 = setPoint1 / 10;
    write_to_eeprom_setPoint1(setPoint1);
  }
  // ... in the future

  if (message_from_pc == "get_relay_0_state") {
    int state = quadRelay.getState(1);
    Serial.println(state);  // 0 = off, 1 = on
  }
  if (message_from_pc == "get_relay_1_state") {
    int state = quadRelay.getState(2);
    Serial.println(state);  // 0 = off, 1 = on
  }
  if (message_from_pc == "get_relay_2_state") {
    int state = quadRelay.getState(3);
    Serial.println(state);  // 0 = off, 1 = on
  }
  if (message_from_pc == "get_relay_3_state") {
    int state = quadRelay.getState(4);
    Serial.println(state);  // 0 = off, 1 = on
  }
  if (message_from_pc == "get_relay_4_state") {
    int state = quadRelay2.getState(1);
    Serial.println(state);  // 0 = off, 1 = on
  }
  if (message_from_pc == "get_relay_5_state") {
    int state = quadRelay2.getState(2);
    Serial.println(state);  // 0 = off, 1 = on
  }
  if (message_from_pc == "get_relay_6_state") {
    int state = quadRelay2.getState(3);
    Serial.println(state);  // 0 = off, 1 = on
  }
  if (message_from_pc == "get_relay_7_state") {
    int state = quadRelay2.getState(4);
    Serial.println(state);  // 0 = off, 1 = on
  }
  if (message_from_pc == "get_relay_8_state") {
    int state = solidStateRelay.getState(1);
    Serial.println(state);  // 0 = off, 1 = on
  }
  if (message_from_pc == "get_relay_9_state") {
    int state = solidStateRelay.getState(2);
    Serial.println(state);  // 0 = off, 1 = on
  }

  else {
    Serial.println("Unknown command: " + message_from_pc);
  }
}

void ultrasound(float ultrasound_time) {
  // flip relay on
  delay(ultrasound_time);
  // Flip relay off
  Serial.println("#");  // '#' indicates process is done
}

void drain(float drain_time) {
  // Do something
  Serial.println("#");  // '#' indicates process is done
}
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

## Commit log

2024-05-18 Updated arduino code to accept communication
2024-06-19 calibration script correction
2024-06-19 Updating calibration script
2024-06-19 Changing BANG value to 2 degrees instead of 5 to avoid overshooting of temperature
2024-06-20 Setting temperature to 0 for cartridge 0
2024-06-21 Updating pump calibration values for pump 0-2
2024-06-24 new pump calibration
2024-06-24 calibration pumop
2024-06-27 Updating workflow
    [metadata.csv]
2024-06-27 nis latest run
    [metadata.csv]
2024-06-27 Adding arduino cleaning procedure for electrodes
2024-06-28 Adding electrodeposition time as variable
2024-06-28 Adding electrodeposition time as variable and reformatting
2024-06-28 Uploading last changes
    [30 0 CP 200 mA cm-2 dc_data.csv, 30 1 CV 25x 200mV s-1 dc_data.csv, 30 Ref CV before.csv, 30 Ref EIS before.csv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]
2024-06-28 changing height of testing electrode
2024-06-28 upload changes
    [30 2 CV 2x 10mV s-1 dc_data.csv, 30 3 EIS ac_data.csv]
2024-06-28 uploading data
    [32 3 EIS ac_data.csv, 32 Ref CV before.csv, 32 Ref EIS before.csv, metadata.csv]
2024-07-01 Fixing bugs
    [39 Electrodeposition dc_data.csv, 40 3 EIS ac_data.csv, 40 Electrodeposition dc_data.csv, 40 Ref CV before.csv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]
2024-07-01 Working workflow
    [44 3 EIS ac_data.csv, 45 3 EIS ac_data.csv, 45 Ref CV before.csv, 45 Ref EIS before.csv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]
2024-07-01 updating recipe
    [48 Electrodeposition dc_data.csv]
2024-07-01 Adding electrodeposition temperature
    [48 3 EIS ac_data.csv, 48 4 CP 100 mA cm-2 dc_data.csv, 48 5 CP 50 mA cm-2 dc_data.csv, 48 6 CP 20 mA cm-2 dc_data.csv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]
2024-07-01 updating temperature
    [metadata.csv]
2024-07-02 comitting logs
    [metadata.csv]
2024-07-02 admiral errors still
    [63 Electrodeposition dc_data.csv, 64 Electrodeposition dc_data.csv, 65 Ref CV before.csv, 65 Ref EIS before.csv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]
2024-07-02 going home
    [metadata.csv]
2024-07-04 Uploading perferct runs
    [72 0 CP 200 mA cm-2 dc_data.csv, 72 1 CV 25x 200mV s-1 dc_data.csv, 72 10 CP 1 mA cm-2 dc_data.csv, 72 11 CV 2x 10mV s-1 dc_data.csv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]
2024-07-06 new experiment with galvanostatic measurement
    [metadata.csv]
2024-07-06 Updated metadata and workflow
    [metadata.csv]
2024-07-06 Updating loop in main
    [metadata.csv]
2024-07-06 finishing recipe
    [metadata.csv]
2024-07-06 Fixing OCV recipe
    [metadata.csv]
2024-07-06 uloading data
    [91 -1 Electrodeposition dc_data.csv, 91 -2 Cathodic scan 1x 10mV s-1 dc_data.csv, 91 -3 OCV scan 1x 10mV s-1 dc_data.csv, 91 0 CP 200 mA cm-2 dc_data.csv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]
2024-07-06 more data
    [metadata.csv]
2024-07-06 uploading latest data
    [95 -1 Electrodeposition dc_data.csv, 95 -2 Cathodic scan 1x 10mV s-1 dc_data.csv, 95 -3 OCV scan 1x 10mV s-1 dc_data.csv, 95 0 CP 200 mA cm-2 dc_data.csv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]
2024-07-07 Temporary measurement of electrodeposition only
2024-07-10 Uploading cleaned metadata, experiment in prograss and plotting with logarithmic plots
    [metadata.csv]
2024-07-11 Arduino boot wait time and recipe in main
2024-07-12 Fixing experiment volume readings
    [126 -1 Electrodeposition dc_data.csv, 126 -2 Cathodic scan 1x 10mV s-1 dc_data.csv, 126 -3 OCV scan 1x 10mV s-1 dc_data.csv, 126 0 CP 200 mA cm-2 dc_data.csv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]
2024-07-13 Uploading another run
    [127 -1 Electrodeposition dc_data.csv, 127 -2 Cathodic scan 1x 10mV s-1 dc_data.csv, 127 -3 OCV scan 1x 10mV s-1 dc_data.csv, 127 Ref CV before.csv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]
2024-07-13 cleaning up data files and making emergency electrode return of potentiostat fails
    [100 -1 Electrodeposition dc_data.csv, 100 -2 Cathodic scan 1x 10mV s-1 dc_data.csv, 100 -3 OCV scan 1x 10mV s-1 dc_data.csv, 101 -1 Electrodeposition dc_data.c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]
2024-07-13 sync data and erros
    [130 -1 Electrodeposition dc_data.csv, 130 -2 Cathodic scan 1x 10mV s-1 dc_data.csv, 130 -3 OCV scan 1x 10mV s-1 dc_data.csv, 130 0 CP 200 mA cm-2 dc_data.csv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]
2024-07-14 up with data
    [141 -1 Electrodeposition dc_data.csv, 141 -2 Cathodic scan 1x 10mV s-1 dc_data.csv, 141 -3 OCV scan 1x 10mV s-1 dc_data.csv, 141 0 CP 200 mA cm-2 dc_data.csv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]
2024-07-16 last update
    [metadata.csv]
2024-07-18 filled the water
    [156 -1 OCV scan 1x 10mV s-1 dc_data.csv, 156 -2 Electrodeposition dc_data.csv, 156 0 CP 200 mA cm-2 dc_data.csv, 156 1 CV 25x 200mV s-1 dc_data.csv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]
2024-08-02 new runs (batch 3)
    [159 -1 OCV scan 1x 10mV s-1 dc_data.csv, 159 -2 Electrodeposition dc_data.csv, 159 0 CP 200 mA cm-2 dc_data.csv, 159 1 CV 25x 200mV s-1 dc_data.csv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]
2024-08-02 new runs
    [171 -1 OCV scan 1x 10mV s-1 dc_data.csv, 171 -2 Electrodeposition dc_data.csv, 171 0 CP 200 mA cm-2 dc_data.csv, 171 1 CV 25x 200mV s-1 dc_data.csv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]
2024-08-29 new experiments
    [201 -1 OCV scan 1x 10mV s-1 dc_data.csv, 201 -2 Electrodeposition dc_data.csv, 201 0 CP 200 mA cm-2 dc_data.csv, 201 1 CV 25x 200mV s-1 dc_data.csv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]
2024-09-03 new data - daniel
    [240 -1 OCV scan 1x 10mV s-1 dc_data.csv, 240 -2 Electrodeposition dc_data.csv, 240 0 CP 200 mA cm-2 dc_data.csv, 240 1 CV 25x 200mV s-1 dc_data.csv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]
2024-09-19 Cleaning the metadata
    [metadata.csv]
2024-10-30 Removing data and fixing Admiral potentiostat issue
    [100 -1 Electrodeposition dc_data.csv, 100 -2 Cathodic scan 1x 10mV s-1 dc_data.csv, 100 -3 OCV scan 1x 10mV s-1 dc_data.csv, 101 -1 Electrodeposition dc_data.c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]
2025-01-08 started taking new data - bare Ni
    [248 -1 OCV scan 1x 10mV s-1 dc_data.csv, 248 -2 Electrodeposition dc_data.csv, 248 0 CP 200 mA cm-2 dc_data.csv, 248 1 CV 25x 200mV s-1 dc_data.csv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]
2025-01-11 Uploading manuals
    [Canada Electrodeposition Bill of Materials (BOM).xlsx]
2025-01-11 Uploading 3D files
    [0 base_tile v11.f3d, 0 base_tile v11.step, 0 base_tile v11.stl, 1 arduino_and_screen_tile v12.stl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]
2025-01-13 run bare Ni again
    [264 -1 OCV scan 1x 10mV s-1 dc_data.csv, 264 -2 Electrodeposition dc_data.csv, 270 -1 OCV scan 1x 10mV s-1 dc_data.csv, 270 -2 Electrodeposition dc_data.csv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]
2025-01-17 newest experiments - Ni foil only - 276 failed
    [276 -1 OCV scan 1x 10mV s-1 dc_data.csv, 276 -2 Electrodeposition dc_data.csv, 276 0 CP 200 mA cm-2 dc_data.csv, 276 1 CV 25x 200mV s-1 dc_data.csv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]
2025-01-17 final Ni substrate only results
    [286 -1 OCV scan 1x 10mV s-1 dc_data.csv, 286 -2 Electrodeposition dc_data.csv, 286 0 CP 200 mA cm-2 dc_data.csv, 286 1 CV 25x 200mV s-1 dc_data.csv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]
2025-01-20 Ni deposition on Ni foil
    [288 -1 OCV scan 1x 10mV s-1 dc_data.csv, 288 -2 Electrodeposition dc_data.csv, 288 0 CP 200 mA cm-2 dc_data.csv, 288 1 CV 25x 200mV s-1 dc_data.csv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]
2025-01-21 NiFe deposition with one fail
    [297 -1 OCV scan 1x 10mV s-1 dc_data.csv, 297 -2 Electrodeposition dc_data.csv, 297 0 CP 200 mA cm-2 dc_data.csv, 297 1 CV 25x 200mV s-1 dc_data.csv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]
2025-01-21 Finalized NiFe and ran 3 runs of all metals
    [301 -1 OCV scan 1x 10mV s-1 dc_data.csv, 301 -2 Electrodeposition dc_data.csv, 301 0 CP 200 mA cm-2 dc_data.csv, 301 1 CV 25x 200mV s-1 dc_data.csv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]
2025-01-21 added two more all metal results and two more NiFe
    [306 -1 OCV scan 1x 10mV s-1 dc_data.csv, 306 -2 Electrodeposition dc_data.csv, 306 0 CP 200 mA cm-2 dc_data.csv, 306 1 CV 25x 200mV s-1 dc_data.csv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]
2025-01-30 added Ni deposition and NiFe deposition
    [316 -1 OCV scan 1x 10mV s-1 dc_data.csv, 316 -2 Electrodeposition dc_data.csv, 316 0 CP 200 mA cm-2 dc_data.csv, 316 1 CV 25x 200mV s-1 dc_data.csv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]
2025-04-11 Removing data, preparing for release
    [248 -1 OCV scan 1x 10mV s-1 dc_data.csv, 248 -2 Electrodeposition dc_data.csv, 248 0 CP 200 mA cm-2 dc_data.csv, 248 1 CV 25x 200mV s-1 dc_data.csv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]
